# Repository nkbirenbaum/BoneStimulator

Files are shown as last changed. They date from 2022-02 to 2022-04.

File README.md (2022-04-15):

# bone-stimulator
Bone stimulator project w/ Saad Javeed

## PCB versions

+ bone_stim_v0  
  + Original constant bone stimulator circuit created by electronics shop  
  + Much larger and not designed to be implantable  
  + Potentiometer allowed for adjustment of stimulation current  
+ bone_stim_v1  
  + Nathan's edit of v0 circuit that makes circuit smaller and stimulation constant  
  + Used by Jawad Khalifeh in trial studies  
+ bone_stim_pulsed_v2  
  + Nathan's redesign for Saad Javeed based on literature ([Cho et al 2018](https://doi.org/10.1016/j.spinee.2018.12.011))  
  + Incorporates stimulator circuit controlled by ATTINY for pulsed stimulation  
  + Did not work on initial testing 4/12 and needed to be resized anyway (printed square from expressPCB)  
+ bone_stim_pulsed_v3  
  + Redesigned to have round edges and an incorporated schematic file  
  + Described below and should be used in future runs  

## Software versions

- Note: software versions do not correlate with PCB versions  
- bone_stim_v1  
  - Uses delay and delayMicroseconds (delay is not very accurate)  
- bone_stim_v2  
  - Uses if(millis() - time_now_ms > PULSE_PERIOD_MS) condition with time_now_ms as unsigned long  
- bone_stim_v3  
  - WORK IN PROGRESS  
  - Need to add button push and blinking funcitonality  
  - Need to sleep in between pulses  
  - Measure current draw if possible  

## Paper

+ "Effect of the type of electrical stimulation on spinal fusion in a rat posterolateral spinal fusion model" Pyung Goo Cho, MD, Gyu Yeol Ji, PhD, Yoon Ha, PhD, Hye Yeong Lee, Dong Ah Shin, MD, PhD. December 22, 2018 DOI: https://doi.org/10.1016/j.spinee.2018.12.011  
+ Link: [The Spine Journal](https://www.thespinejournalonline.com/article/S1529-9430(18)31320-2/fulltext)  
+ Circuit from paper  

# PCB design

- bone_stim_pulsed_v3 finalized by NKB 04/14/2022.  
- Gerber and drill files for ordering boards are available in the "bone_stim_pulsed_v3" folder.  

board v3  
<sup>bone stim pulsed v3 PCB </sup>  

schematic v3  
<sup>bone stim pulsed v3 schematic</sup>  

## Parts, datasheets, and schematics

+ Microcontroller
  + ATTINY13-10SSU ([DigiKey](https://www.digikey.com/en/products/detail/microchip-technology/ATTINY13V-10SSU/1008458) / [datasheet](https://ww1.microchip.com/downloads/en/DeviceDoc/2535S.pdf))  
  + ATTINY programming clip ([Amazon](https://www.amazon.com/Pomona-Electronics-5250-Plated-Spacing/dp/B00JJ4G13I/ref=sr_1_3?keywords=soic8+clip&qid=1645148900&sr=8-3))  
  + ATTINY pinout  
    ATTINY13 pinout  

- Current source
  - LM334 ([DigiKey](https://www.digikey.com/en/products/detail/texas-instruments/LM334M/3701392) / [datasheet](https://www.ti.com/general/docs/suppproductinfo.tsp?distId=10&gotoUrl=https%3A%2F%2Fwww.ti.com%2Flit%2Fgpn%2Flm134))  

+ Pushbutton
  + EVQ-3PLA15 ([Digikey](https://www.digikey.com/en/products/detail/panasonic-electronic-components/EVQ-3PLA15/7561411?s=N4IgTCBcDaIAoEYxgCwGYBsBhAKgWgDkAREAXQF8g) / [datasheet](https://www3.panasonic.biz/ac/e_download/control/switch/light-touch/catalog/sw_lt_eng_49s.pdf))  

- LED
  - LS P476-Q1R2-1-0-20-R18-Z ([Digikey](https://www.digikey.com/en/products/detail/osram-opto-semiconductors-inc/LS-P476-Q1R2-1-0-20-R18-Z/7325513?s=N4IgjCBcoMxgnFUBjKAzAhgGwM4FMAaEAeygG1wYAmABhoHYQiBWADnpkaIDYwxmYTENyphuAFiFj2VKlKrUaiImAXjmzecwXd54kV3BVu8cYJUwaYeroC6RAA4AXKCADKTgE4BLAHYBzEABfFjMkEFRITFxCEnIQDmYJKTMaJKlWcRpuViFaOhMhHNYYcwSONKFMtLLTZnpJFTpLQXsQZ1cPHwDgnkzwyOj8IlJICjBqnJA2jsh3Lz9AkPBmOgH0bGG4sfAEbKE2VSKaBSL%2BZWFRC4l9IXolCCJ6MBO7-ho3jTuqcUfy56qNF%2BVVY%2BxmLjmXUWvRAAFo5NAIlAvABXWKjCiaWxBZYIig4AC2ABMAARYPCkzwUknTHjhbxE1ywl5-WYgIROACeDjwrgwOFQOKAA) / [datasheet](https://dammedia.osram.info/media/resource/hires/osram-dam-2493611/LS%20P476.pdf))  

+ Battery
  + CR-2450/H1AN ([Digikey](https://www.digikey.com/en/products/detail/panasonic-bsg/CR-2450-H1AN/2404067?s=N4IgTCBcDaIMYCcC0YAsBWADAegBIEYBBAORAF0BfIA) / [datasheet](https://b2b-api.panasonic.eu/file_stream/pids/fileversion/3648))
  + Search [Digikey](https://www.digikey.com/en/products/filter/batteries-non-rechargeable-primary/90?s=N4IgjCBcoMwExVAYygMwIYBsDOBTANCAPZQDaIM8YYMIhlc1ADHRVdaw9QgLqEAOAFyggAyoIBOASwB2AcxABferWggUkDDgLEy4AKwA2AJwAOCITD6A7KbiHWN-QBYmtS4abXr%2B1mEPOgQiEzt6h7uCGUaYRYHYwzsEgznampsZ%2BptYw1hmWxlZwEUWGdhYgcM5gRXkViV7FzuyslU3WDoSVAcbOLfr66bVwNsbW5cNZ1knDxgVDhjUs9ExwwxB8IEIi4tLySp0DiOpoWHiEJJDkMKYpTZw3N70bW5BikrIKyhVeGWoaWmddJcKAACABqnAAdHBwVDDLDnsJXgBVGRSQQAeVQAFlcOhsABXCS4fYgAC0CD%2BUEkBJ0F3Ivh4ii%2BlPISCIshBSFwmEwIIARuhBIJcBIAJ4gJlAA) for other batteries if out of stock (this search saves most of the relevant parameters but check pin spacing with PCB)  

- Capacitor
  - 1 µF, 0805 (2012 metric) packaging ([DigiKey](https://www.digikey.com/en/products/detail/kemet/C0805C105K5PAC7800/6097177?s=N4IgTCBcDaIMYAYAcCCscCMaDWqAOAhnAOwoIgC6AvkA))

+ Resistors
  + 1 kΩ, 0603 (1508 metric) packaging  
  + 200 Ω, 0603 (1508 metric) packaging  
  + 680 Ω, 0603 (1508 metric) packaging  
  + Sourced from [resistor sample book](https://www.amazon.com/Yobett-15pF-1uF-3725pcs-Resistor-Capacitor/dp/B00IN2314E/ref=sr_1_10?crid=UE07MO30ZN0Y&keywords=smd+resistor+variety+pack+0603&qid=1649957977&sprefix=smd+resistor+variety+pack+0603%2Caps%2C92&sr=8-10)

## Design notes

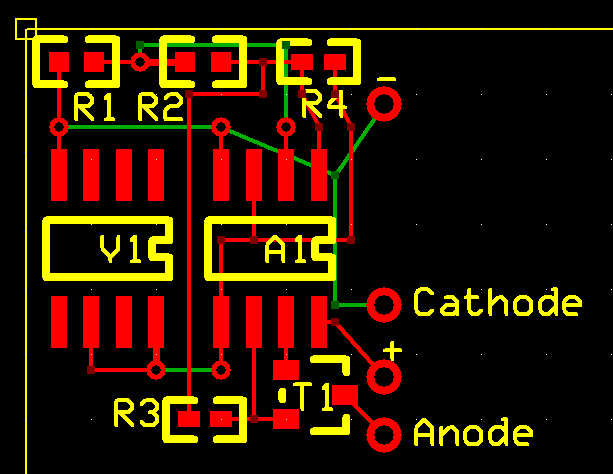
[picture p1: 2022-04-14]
bone_stim_v1/PCB Image.PNG

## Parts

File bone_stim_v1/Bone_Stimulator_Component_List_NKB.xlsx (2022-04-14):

PCB Code | Item | Price (10+) | PCB Footprint | Purchase Link
R1 | 1 MΩ resistor | $0.16 | SMT 0603 | http://www.mouser.com/ProductDetail/TE-Connectivity-Neohm/CPF0603B1M0E1/?qs=sGAEpiMZZMu61qfTUdNhGxAfPTOoMd3MAck7XqNKwxI%3d
R2 | 221 kΩ resistor | $0.20 | SMT 0603 | http://www.mouser.com/ProductDetail/Welwyn-Components-TT-Electronics/PCF0603R-221KBT1/?qs=sGAEpiMZZMu61qfTUdNhGy9OQ91HnoNziftfzSswnTU%3d
R3 | 5.49 kΩ resistor | $0.22 | SMT 0402 | http://www.mouser.com/ProductDetail/TE-Connectivity-Neohm/CPF0402B5K49E1/
R4 | 24.0 kΩ resistor | $0.22 | SMT 0402 | http://www.mouser.com/ProductDetail/TE-Connectivity-Neohm/CPF0402B24KE1/?qs=sGAEpiMZZMu61qfTUdNhGxAfPTOoMd3MIlCA6dfBD8g%3d
T1 | BC860 pnp transistor | $0.16 | SMT SOT-23 3 pin | http://www.mouser.com/ProductDetail/Fairchild-Semiconductor/BC860BMTF/?qs=ljbEvF4DwOP5zgVvN%2Fzv3Q%3D%3D
V1 | LT 1004-1.2 reference | $0.78 | SMT SOIC 0.050 pitch - 8 pin | http://www.mouser.com/ProductDetail/Texas-Instruments/LT1004CDR-1-2/?qs=sGAEpiMZZMtYFXwiBRPs084jNrzvyjkK
A1 | TS942AIDT op-amp | $0.82 | SMT SOIC 0.050 pitch - 8 pin | http://www.mouser.com/ProductDetail/STMicroelectronics/TS942AIDT/

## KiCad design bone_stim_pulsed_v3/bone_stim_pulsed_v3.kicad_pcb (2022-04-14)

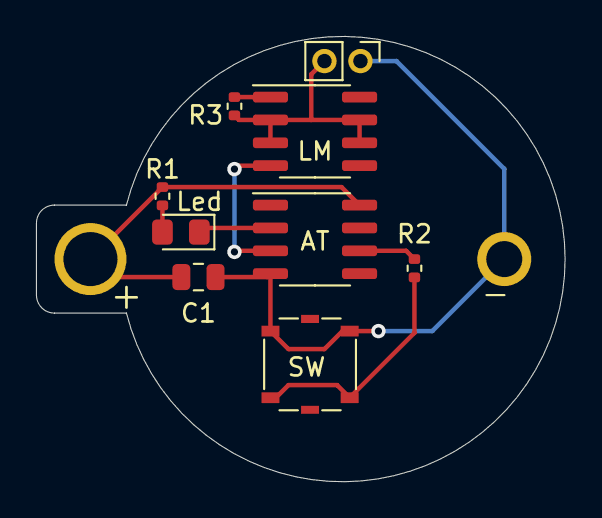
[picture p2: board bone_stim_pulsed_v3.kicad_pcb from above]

Board: 2 copper layers, 29.4 x 24.7 mm, 10 parts (0 on the bottom side), 9 nets.

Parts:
 : 3.3V; BatteryHolder_Keystone_105_1x2430
 #2: Conn; PinHeader_1x02_P2.00mm_Vertical
AT: ATtiny13V-10SSU; SOIC-8_3.9x4.9mm_P1.27mm
C1: 1 μF; C_0805_2012Metric
LM: LM334M; SOIC-8_3.9x4.9mm_P1.27mm
Led: Red; LED_0805_2012Metric_Pad1.15x1.40mm_HandSolder
R1: 1 kΩ; R_0402_1005Metric
R2: 200 Ω; R_0402_1005Metric
R3: 680 Ω; R_0402_1005Metric
SW: SW_SPST_Panasonic_EVQPL_3PL_5PL_PT_A15

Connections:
+3V3: .1, AT.8, C1.1, R1.1
GND: .2, #2.1, AT.4, C1.2, SW.1
unnamed: AT.2, Led.1
unnamed: AT.3, LM.4
unnamed: AT.6, R2.2
unnamed: Led.2, R1.2
unnamed: LM.1, R3.2
unnamed: #2.2, LM.2, LM.3, LM.6, LM.7, R3.1
unnamed: R2.1, SW.2

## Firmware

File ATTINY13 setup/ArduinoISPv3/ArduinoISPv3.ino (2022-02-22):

// From https://github.com/PaulStoffregen/Arduino-1.0.6-Teensyduino/blob/master/build/shared/examples/ArduinoISP/ArduinoISP.ino
// Arduino ISP with SPI included

// ArduinoISP
// Copyright (c) 2008-2011 Randall Bohn
// If you require a license, see
// https://opensource.org/licenses/bsd-license.php
//
// This sketch turns the Arduino into a AVRISP using the following Arduino pins:
//
// Pin 10 is used to reset the target microcontroller.
//
// By default, the hardware SPI pins MISO, MOSI and SCK are used to communicate
// with the target. On all Arduinos, these pins can be found
// on the ICSP/SPI header:
//
//               MISO °. . 5V (!) Avoid this pin on Due, Zero...
//               SCK   . . MOSI
//                     . . GND
//
// On some Arduinos (Uno,...), pins MOSI, MISO and SCK are the same pins as
// digital pin 11, 12 and 13, respectively. That is why many tutorials instruct
// you to hook up the target to these pins. If you find this wiring more
// practical, have a define USE_OLD_STYLE_WIRING. This will work even when not
// using an Uno. (On an Uno this is not needed).
//
// Alternatively you can use any other digital pin by configuring
// software ('BitBanged') SPI and having appropriate defines for PIN_MOSI,
// PIN_MISO and PIN_SCK.
//
// IMPORTANT: When using an Arduino that is not 5V tolerant (Due, Zero, ...) as
// the programmer, make sure to not expose any of the programmer's pins to 5V.
// A simple way to accomplish this is to power the complete system (programmer
// and target) at 3V3.
//
// Put an LED (with resistor) on the following pins:
// 9: Heartbeat   - shows the programmer is running
// 8: Error       - Lights up if something goes wrong (use red if that makes sense)
// 7: Programming - In communication with the slave
//

#include "Arduino.h"
#undef SERIAL


#define PROG_FLICKER true

// Configure SPI clock (in Hz).
// E.g. for an ATtiny @ 128 kHz: the datasheet states that both the high and low
// SPI clock pulse must be > 2 CPU cycles, so take 3 cycles i.e. divide target
// f_cpu by 6:
//     #define SPI_CLOCK            (128000/6)
//
// A clock slow enough for an ATtiny85 @ 1 MHz, is a reasonable default:

#define SPI_CLOCK 		(1000000/6)


// Select hardware or software SPI, depending on SPI clock.
// Currently only for AVR, for other architectures (Due, Zero,...), hardware SPI
// is probably too fast anyway.

#if defined(ARDUINO_ARCH_AVR)

  #if SPI_CLOCK > (F_CPU / 128)
    #define USE_HARDWARE_SPI
  #endif

#endif

// Configure which pins to use:

// The standard pin configuration.
#ifndef ARDUINO_HOODLOADER2

  #define RESET     10 // Use pin 10 to reset the target rather than SS
  #define LED_HB    9
  #define LED_ERR   8
  #define LED_PMODE 7

  // Uncomment following line to use the old Uno style wiring
  // (using pin 11, 12 and 13 instead of the SPI header) on Leonardo, Due...

  #define USE_OLD_STYLE_WIRING

  #ifdef USE_OLD_STYLE_WIRING

    #define PIN_MOSI	11
    #define PIN_MISO	12
    #define PIN_SCK		13

  #endif

  // HOODLOADER2 means running sketches on the ATmega16U2 serial converter chips
  // on Uno or Mega boards. We must use pins that are broken out:
#else

  #define RESET     	4
  #define LED_HB    	7
  #define LED_ERR   	6
  #define LED_PMODE 	5

#endif

// By default, use hardware SPI pins:
#ifndef PIN_MOSI
  #define PIN_MOSI 	MOSI
#endif

#ifndef PIN_MISO
  #define PIN_MISO 	MISO
#endif

#ifndef PIN_SCK
  #define PIN_SCK 	SCK
#endif

// Force bitbanged SPI if not using the hardware SPI pins:
#if (PIN_MISO != MISO) ||  (PIN_MOSI != MOSI) || (PIN_SCK != SCK)
  #undef USE_HARDWARE_SPI
#endif


// Configure the serial port to use.
//
// Prefer the USB virtual serial port (aka. native USB port), if the Arduino has one:
//   - it does not autoreset (except for the magic baud rate of 1200).
//   - it is more reliable because of USB handshaking.
//
// Leonardo and similar have an USB virtual serial port: 'Serial'.
// Due and Zero have an USB virtual serial port: 'SerialUSB'.
//
// On the Due and Zero, 'Serial' can be used too, provided you disable autoreset.
// To use 'Serial': #define SERIAL Serial

#ifdef SERIAL_PORT_USBVIRTUAL
  #define SERIAL SERIAL_PORT_USBVIRTUAL
#else
  #define SERIAL Serial
#endif


// Configure the baud rate:

#define BAUDRATE	19200
// #define BAUDRATE	115200
// #define BAUDRATE	1000000


#define HWVER 2
#define SWMAJ 1
#define SWMIN 18

// STK Definitions
#define STK_OK      0x10
#define STK_FAILED  0x11
#define STK_UNKNOWN 0x12
#define STK_INSYNC  0x14
#define STK_NOSYNC  0x15
#define CRC_EOP     0x20 //ok it is a space...

void pulse(int pin, int times);

#ifdef USE_HARDWARE_SPI
#include "SPI.h"
#else

#define SPI_MODE0 0x00

#if !defined(ARDUINO_API_VERSION) || ARDUINO_API_VERSION != 10001 // A SPISettings class is declared by ArduinoCore-API 1.0.1
class SPISettings {
  public:
    // clock is in Hz
    SPISettings(uint32_t clock, uint8_t bitOrder, uint8_t dataMode) : clockFreq(clock) {
      (void) bitOrder;
      (void) dataMode;
    };

    uint32_t getClockFreq() const {
      return clockFreq;
    }

  private:
    uint32_t clockFreq;
};
#endif  // !defined(ARDUINO_API_VERSION)

class BitBangedSPI {
  public:
    void begin() {
      digitalWrite(PIN_SCK, LOW);
      digitalWrite(PIN_MOSI, LOW);
      pinMode(PIN_SCK, OUTPUT);
      pinMode(PIN_MOSI, OUTPUT);
      pinMode(PIN_MISO, INPUT);
    }

    void beginTransaction(SPISettings settings) {
      pulseWidth = (500000 + settings.getClockFreq() - 1) / settings.getClockFreq();
      if (pulseWidth == 0) {
        pulseWidth = 1;
      }
    }

    void end() {}

    uint8_t transfer(uint8_t b) {
      for (unsigned int i = 0; i < 8; ++i) {
        digitalWrite(PIN_MOSI, (b & 0x80) ? HIGH : LOW);
        digitalWrite(PIN_SCK, HIGH);
        delayMicroseconds(pulseWidth);
        b = (b << 1) | digitalRead(PIN_MISO);
        digitalWrite(PIN_SCK, LOW); // slow pulse
        delayMicroseconds(pulseWidth);
      }
      return b;
    }

  private:
    unsigned long pulseWidth; // in microseconds
};

static BitBangedSPI SPI;

#endif

void setup() {
  SERIAL.begin(BAUDRATE);

  pinMode(LED_PMODE, OUTPUT);
  pulse(LED_PMODE, 2);
  pinMode(LED_ERR, OUTPUT);
  pulse(LED_ERR, 2);
  pinMode(LED_HB, OUTPUT);
  pulse(LED_HB, 2);

}

int ISPError = 0;
int pmode = 0;
// address for reading and writing, set by 'U' command
unsigned int here;
uint8_t buff[256]; // global block storage

#define beget16(addr) (*addr * 256 + *(addr+1) )
typedef struct param {
  uint8_t devicecode;
  uint8_t revision;
  uint8_t progtype;
  uint8_t parmode;
  uint8_t polling;
  uint8_t selftimed;
  uint8_t lockbytes;
  uint8_t fusebytes;
  uint8_t flashpoll;
  uint16_t eeprompoll;
  uint16_t pagesize;
  uint16_t eepromsize;
  uint32_t flashsize;
}
parameter;

parameter param;

// this provides a heartbeat on pin 9, so you can tell the software is running.
uint8_t hbval = 128;
int8_t hbdelta = 8;
void heartbeat() {
  static unsigned long last_time = 0;
  unsigned long now = millis();
  if ((now - last_time) < 40) {
    return;
  }
  last_time = now;
  if (hbval > 192) {
    hbdelta = -hbdelta;
  }
  if (hbval < 32) {
    hbdelta = -hbdelta;
  }
  hbval += hbdelta;
  analogWrite(LED_HB, hbval);
}

static bool rst_active_high;

void reset_target(bool reset) {
  digitalWrite(RESET, ((reset && rst_active_high) || (!reset && !rst_active_high)) ? HIGH : LOW);
}

void loop(void) {
  // is pmode active?
  if (pmode) {
    digitalWrite(LED_PMODE, HIGH);
  } else {
    digitalWrite(LED_PMODE, LOW);
  }
  // is there an error?
  if (ISPError) {
    digitalWrite(LED_ERR, HIGH);
  } else {
    digitalWrite(LED_ERR, LOW);
  }

  // light the heartbeat LED
  heartbeat();
  if (SERIAL.available()) {
    avrisp();
  }
}

uint8_t getch() {
  while (!SERIAL.available());
  return SERIAL.read();
}
void fill(int n) {
  for (int x = 0; x < n; x++) {
    buff[x] = getch();
  }
}

#define PTIME 30
void pulse(int pin, int times) {
  do {
    digitalWrite(pin, HIGH);
    delay(PTIME);
    digitalWrite(pin, LOW);
    delay(PTIME);
  } while (times--);
}

void prog_lamp(int state) {
  if (PROG_FLICKER) {
    digitalWrite(LED_PMODE, state);
  }
}

uint8_t spi_transaction(uint8_t a, uint8_t b, uint8_t c, uint8_t d) {
  SPI.transfer(a);
  SPI.transfer(b);
  SPI.transfer(c);
  return SPI.transfer(d);
}

void empty_reply() {
  if (CRC_EOP == getch()) {
    SERIAL.print((char)STK_INSYNC);
    SERIAL.print((char)STK_OK);
  } else {
    ISPError++;
    SERIAL.print((char)STK_NOSYNC);
  }
}

void breply(uint8_t b) {
  if (CRC_EOP == getch()) {
    SERIAL.print((char)STK_INSYNC);
    SERIAL.print((char)b);
    SERIAL.print((char)STK_OK);
  } else {
    ISPError++;
    SERIAL.print((char)STK_NOSYNC);
  }
}

void get_version(uint8_t c) {
  switch (c) {
    case 0x80:
      breply(HWVER);
      break;
    case 0x81:
      breply(SWMAJ);
      break;
    case 0x82:
      breply(SWMIN);
      break;
    case 0x93:
      breply('S'); // serial programmer
      break;
    default:
      breply(0);
  }
}

void set_parameters() {
  // call this after reading parameter packet into buff[]
  param.devicecode = buff[0];
  param.revision   = buff[1];
  param.progtype   = buff[2];
  param.parmode    = buff[3];
  param.polling    = buff[4];
  param.selftimed  = buff[5];
  param.lockbytes  = buff[6];
  param.fusebytes  = buff[7];
  param.flashpoll  = buff[8];
  // ignore buff[9] (= buff[8])
  // following are 16 bits (big endian)
  param.eeprompoll = beget16(&buff[10]);
  param.pagesize   = beget16(&buff[12]);
  param.eepromsize = beget16(&buff[14]);

  // 32 bits flashsize (big endian)
  param.flashsize = buff[16] * 0x01000000
                    + buff[17] * 0x00010000
                    + buff[18] * 0x00000100
                    + buff[19];

  // AVR devices have active low reset, AT89Sx are active high
  rst_active_high = (param.devicecode >= 0xe0);
}

void start_pmode() {

  // Reset target before driving PIN_SCK or PIN_MOSI

  // SPI.begin() will configure SS as output, so SPI master mode is selected.
  // We have defined RESET as pin 10, which for many Arduinos is not the SS pin.
  // So we have to configure RESET as output here,
  // (reset_target() first sets the correct level)
  reset_target(true);
  pinMode(RESET, OUTPUT);
  SPI.begin();
  SPI.beginTransaction(SPISettings(SPI_CLOCK, MSBFIRST, SPI_MODE0));

  // See AVR datasheets, chapter "SERIAL_PRG Programming Algorithm":

  // Pulse RESET after PIN_SCK is low:
  digitalWrite(PIN_SCK, LOW);
  delay(20); // discharge PIN_SCK, value arbitrarily chosen
  reset_target(false);
  // Pulse must be minimum 2 target CPU clock cycles so 100 usec is ok for CPU
  // speeds above 20 KHz
  delayMicroseconds(100);
  reset_target(true);

  // Send the enable programming command:
  delay(50); // datasheet: must be > 20 msec
  spi_transaction(0xAC, 0x53, 0x00, 0x00);
  pmode = 1;
}

void end_pmode() {
  SPI.end();
  // We're about to take the target out of reset so configure SPI pins as input
  pinMode(PIN_MOSI, INPUT);
  pinMode(PIN_SCK, INPUT);
  reset_target(false);
  pinMode(RESET, INPUT);
  pmode = 0;
}

void universal() {
  uint8_t ch;

  fill(4);
  ch = spi_transaction(buff[0], buff[1], buff[2], buff[3]);
  breply(ch);
}

void flash(uint8_t hilo, unsigned int addr, uint8_t data) {
  spi_transaction(0x40 + 8 * hilo,
                  addr >> 8 & 0xFF,
                  addr & 0xFF,
                  data);
}
void commit(unsigned int addr) {
  if (PROG_FLICKER) {
    prog_lamp(LOW);
  }
  spi_transaction(0x4C, (addr >> 8) & 0xFF, addr & 0xFF, 0);
  if (PROG_FLICKER) {
    delay(PTIME);
    prog_lamp(HIGH);
  }
}

unsigned int current_page() {
  if (param.pagesize == 32) {
    return here & 0xFFFFFFF0;
  }
  if (param.pagesize == 64) {
    return here & 0xFFFFFFE0;
  }
  if (param.pagesize == 128) {
    return here & 0xFFFFFFC0;
  }
  if (param.pagesize == 256) {
    return here & 0xFFFFFF80;
  }
  return here;
}
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

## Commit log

2022-02-22 Add files via upload
    Files for settings up the Arduino Uno as an ISP and the ATTINY13 with a test blink sketch.
2022-04-14 Update README.md
    Added circuit from paper
2022-04-14 Add files via upload
    New design for fabrication 4/14/2022
    [bone_stim_pulsed_v3-B_Cu.gbr, bone_stim_pulsed_v3-B_Mask.gbr, bone_stim_pulsed_v3-B_SilkS.gbr, bone_stim_pulsed_v3-Edge_Cuts.gbr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]
2022-04-14 Add files via upload
    Old design Jawad Khalifeh was using that I designed a while ago.
    [Bone_Stimulator_Component_List_NKB.xlsx]
2022-04-14 Add files via upload
    Old constant stim design from electronics shop
    [50 uAmp Current Source NKB 11_12_2015.sch]
2022-04-14 Update README.md
    added pcb and schematic
